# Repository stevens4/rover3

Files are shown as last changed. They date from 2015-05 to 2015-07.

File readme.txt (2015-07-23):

see documentation/Rover_3_Documentation.pdf

rover 3 functionality

need 6 AI and 12 DO, at least

hardware:
    1x raspberry pi 2 B (27 GPIO pins built in)
    2x thermocouple k-type amplifier
    1x pi breakout ribbon cable
    3x ADS1115 4chan 16b ADC  (interfaces via I2C, are stackable)
    1x power supply
    1x usb cable
    1x SD card, preloaded rasbian

analog inputs (sense):
    water thermocouple
    pooh main foreline pressure
    pooh source foreline pressure
    tigger source foreline pressure
    tigger buffer foreline pressure
    tigger main foreline pressure

digital output (relays):
    pooh water valve
    pooh source roughing
    pooh main roughing
    pooh source diffusion
    pooh main gate valve
    pooh source foreline valve
    tigger source foreline valve
    tigger main gate valve
    tigger diffusion pumps
    tigger main foreline valve
    tigger detector gauge
    tigger water valve

main features that we want:
	- real time logging of all AI & DO channels' values
		+ ability to plot history of values
		+ auto clean-up: compactify log based on age of entry
	- persist state of DIO in absence of pi power
	- automated interlocks 
		+ toggle a relay based on an AI value
		+ dispatch a message (clients, SMS) in this event
		+ add entry to status log
		+ configurable, configuration persists in absence of pi power
	- real time updating of a transcript of actions taken
	- rover client:
		+ subscribed to interlock events and DO toggle events
		+ can request current state of AI & DO

statusFile:
	timestamp:    [states of each DO + values of each AI]
	
transcript:
	timestamp:    [action that occurred in plain text. a capture of stdout]

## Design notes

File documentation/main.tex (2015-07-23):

\documentclass{article}
\usepackage[utf8]{inputenc}

\title{Rover 3 Documentation}
\author{Bobby Stevens}
\date{July 2015}

\usepackage{natbib}
\usepackage{graphicx}
\usepackage{url}
\usepackage{rotating}
\usepackage{multirow}

\begin{document}

\maketitle

\section{Introduction}
Rover is the name designated to the computer in the lab which controls the vacuum pumps and valves for both the Pooh and Tigger chambers. These things are not typically power cycled on a daily basis so their functionality is best contained in an infrequently used computer. Futhermore, these devices need to have interlocks (i.e. automatically be turned off based on some input sensor exceeding a set point) to ensure safe operation.

\subsection{Brief History of Rover}
This is the third incarnation of the Rover machine. The first, and longest running, was built on an Intel 386 based machine and was retired in 2011 after its graphics card failed. Thus ended the ``Good Dog'' era. It was replaced with a Windows XP machine running a LabView program attached to an NI-USB DAQ. This got the job done but had flaws such as requiring a sustained internet connection in order to authenticate LabView. This was the ``Bad Dog'' era. Rover 2 was replaced in 2015 by Rover 3. This marks the beginning of the ``Good Kitty'' era.

\section{Hardware Description}
We have a Raspberry Pi 2 (RP2) computer connected to a custom backplane board that buffers the DIO and provides the A2D chips for measurement by the Pi. The signals for the equipment toggle relays and instrumentation are then sent out to the individual racks for Pooh and Tigger. We will address each of these steps in their own subsection.

\subsection{The Raspberry Pi 2}
Rover 3 is built on a Raspberry Pi 2 model B (RP2). It is running Raspbian (raspberry optimized debian unix) with Gnome 2 installed on top. The RP2 was chosen for its low power consumption (5V @ 1A, max), built in DIO and I2C pins, and more than ample RAM.

Rover 3 interacts with the laboratory equipment through a custom backplane board, see section \ref{sect:backplane}, via its GPIO pins. The pin mapping is shown in figure \ref{fig:gpioPinMapping}. We have purchased a so-called ``cobbler'' board that has a ribbon cable plugged into the GPIO bank and connects to a labeled PCB.

\begin{figure}
\centering
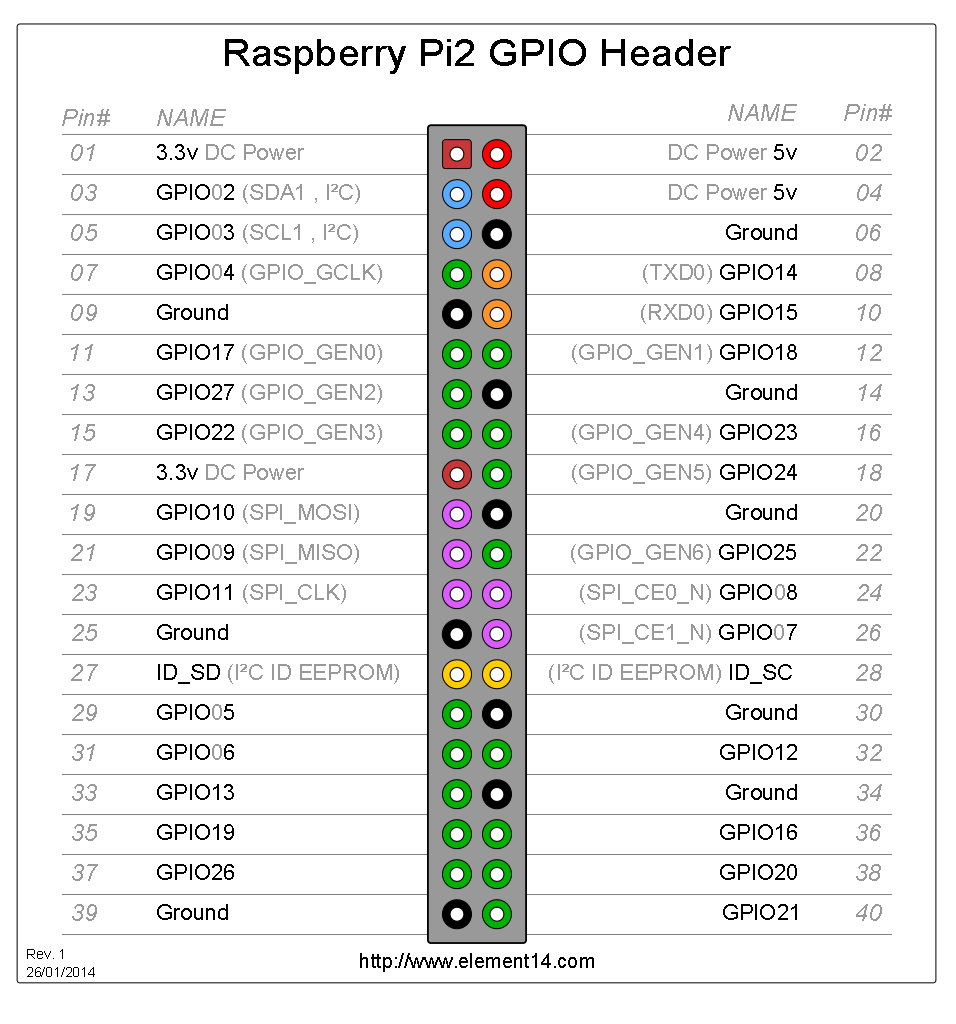
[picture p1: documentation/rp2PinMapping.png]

\caption{A mapping of the GPIO pins on the RP2 board. Interfacing at this level should not be necessary and the same information is printed on the ``cobbler'' board that is mounted to the backplane board. Source: element14.com}
\label{fig:gpioPinMapping}
\end{figure}

The monitor is attached by HDMI. The keyboard and mouse are both USB. Power is provided to the RP2 by a Motorola wall-to-USB transformer (better recognized as a cellphone charger) and plugged into the uninterurptable power supply.

\subsection{The Backplane Board}
\label{sect:backplane}
The RP2 cannot provide enough current on its DIO pins to toggle the relays (16mA max of RP2 compared to .02mA (steady state) and 6mA (switching) for relays). Thus we must buffer these DIO pins if we wish to control multiple relays at once. It also does not have any built-in analog-to-digital converter (ADC) so we will have to provide that functionality and serialize that data in some way. 

The backplane functional diagram is shown in figure \ref{fig:roverBreakout}. An attempt was made to keep the functional diagram and board layout as similar as possible to aid in troubleshooting when the need arises.

\begin{figure}
\centering
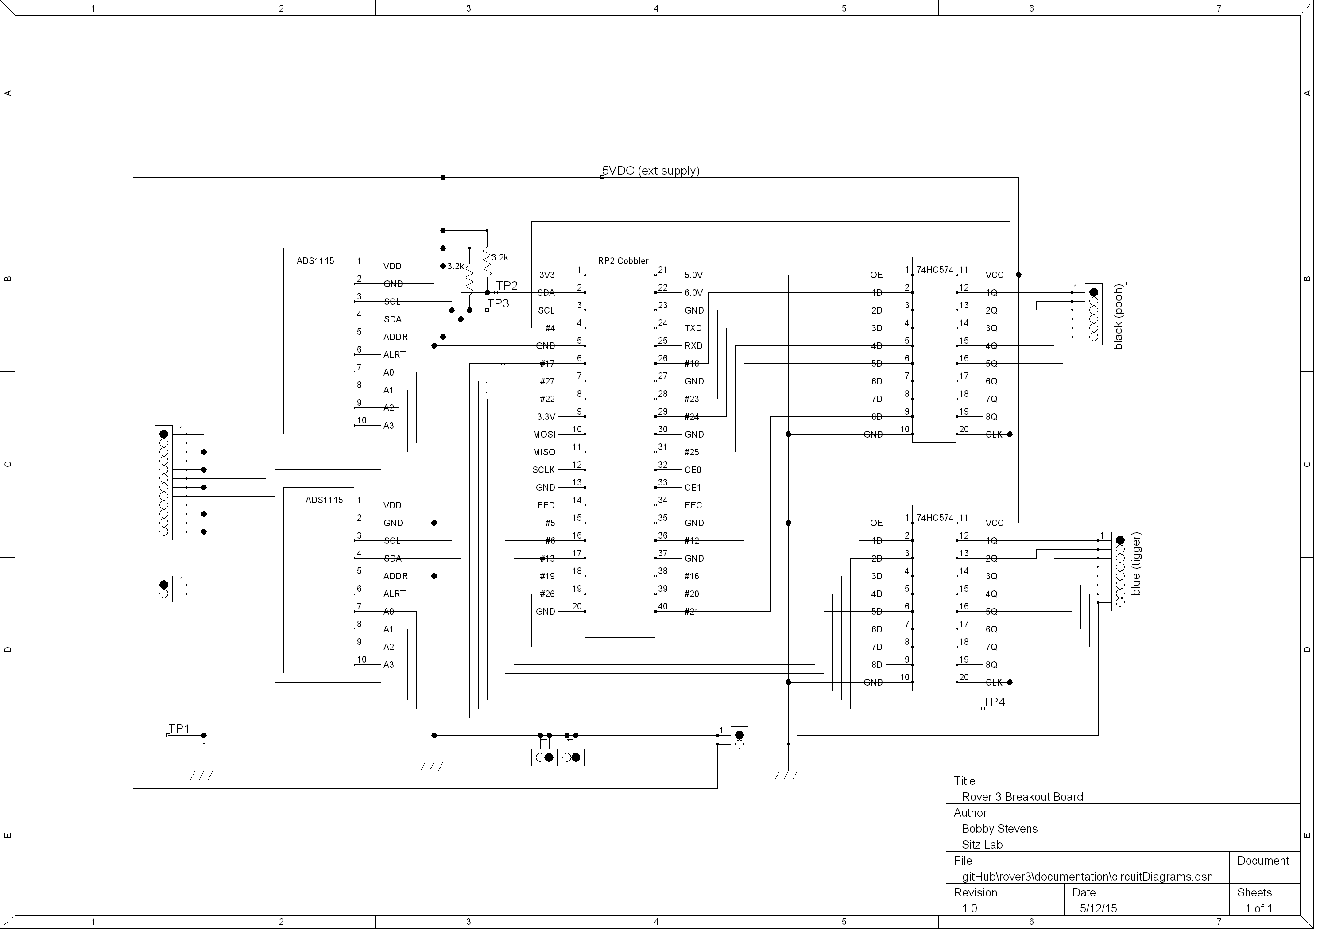
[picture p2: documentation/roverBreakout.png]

\caption{The functional diagram for the RP2 backplane board.}
\label{fig:roverBreakout}
\end{figure}

\subsubsection{DIO Buffering \& Relay Control}
The DIO control is handled on the right side of the backplane board.

A further need for buffering comes from the RP2's DIO reset state on power cycle. When the RP2 is rebooted, its DIO pins get written with an intermediate (TTL) level of 1.5V which is too high to read low and but will be read high by some buffer chips (e.g. 74LS241). This is undesirable because when the RP2 is booting we do not want every piece of equipment to turn on. Thus we use a clockable buffer. The 74HC574 chip has 8 inputs and 8 outputs with a clock pin that will ``write'' the input to the output only on a positive going transition. Thus we design our software (section \ref{sect:software}) to update the proper RP2 DIO pin then use a second DIO pin to clock the buffer thereby pushing that state to the relay or equipment.

The output pins of the 574 are then directly wired to the Pooh (black) and Tigger (blue) screw terminal blocks. The output pin numbers map 1-to-1 with the 574. See figure \ref{fig:roverBreakout}.

\subsubsection{ADC Implementation}
Analog input and digitization is handled on the left side of the backplane board, see figures \ref{fig:roverBreakout} and \ref{fig:roverBreakoutPicTop}.

As previously mentioned, the RP2 does not have any built-in ADC. We have 7 analog inputs that we need to interlock based upon their values. All but one of these needs to be a referenced single-ended (RSE) termination style which will require 6 ADCs. The remaining analog input needs to be measured in differential mode thus requiring 2 ADCs of its own. Thus we need 8 ADCs.

We will never need to respond very quickly to changes on any of these inputs. A response time of a few seconds is more than enough to establish safety with the diffusion pumps which take approximately 45 minutes to cool down anyways. Thus we do not need particularly fast ADCs.

Based on these requirements we can easily get by with a multiplexed ADC (multiple inputs are measured by 1 ADC in serial). TI's ADS1115 is precisely what we need. It has 4 inputs that will be multiplexed to a 16-bit 860SPS ADC. This information will be communicated by the I2C (or $I^2C$) interface. 

I2C is a serialized data communication protocol. This is done over two wires: a data wire (SDA) and a clock wire (SCL). Devices can only pull these wires low so a pull-up resistor is required to improve the time response (resistors R1 and R2 in figure \ref{fig:roverBreakout}). As in other protocols, there is a master and multiple slaves. For I2C each slave has a programmable 7-bit address. In the case of the ADS1115 the address pin will be tied low to make the address be 0x63 or tied high to make the address be 0x64. A key distinction for I2C is that any device can assert the clock pin low. This is important if you wish to truly understand how the communication works.

A timeline of how I2C works follows, refer to figure \ref{fig:i2cTiming} while reading. The master will send on SDA an address that it wants to either read or write from followed by a read/write bit. If that device is powered and on the lines it will respond the next clock cycle with the acknowledge or ``ack'' bit. Messages are limited to 8bits. If a read is specified the slave will load its data onto the SDA and clock SCL. If a write is specified the master will load data onto SDA and clock SCL. For more information on I2C see Horowitz and Hill.

\begin{figure}
\centering
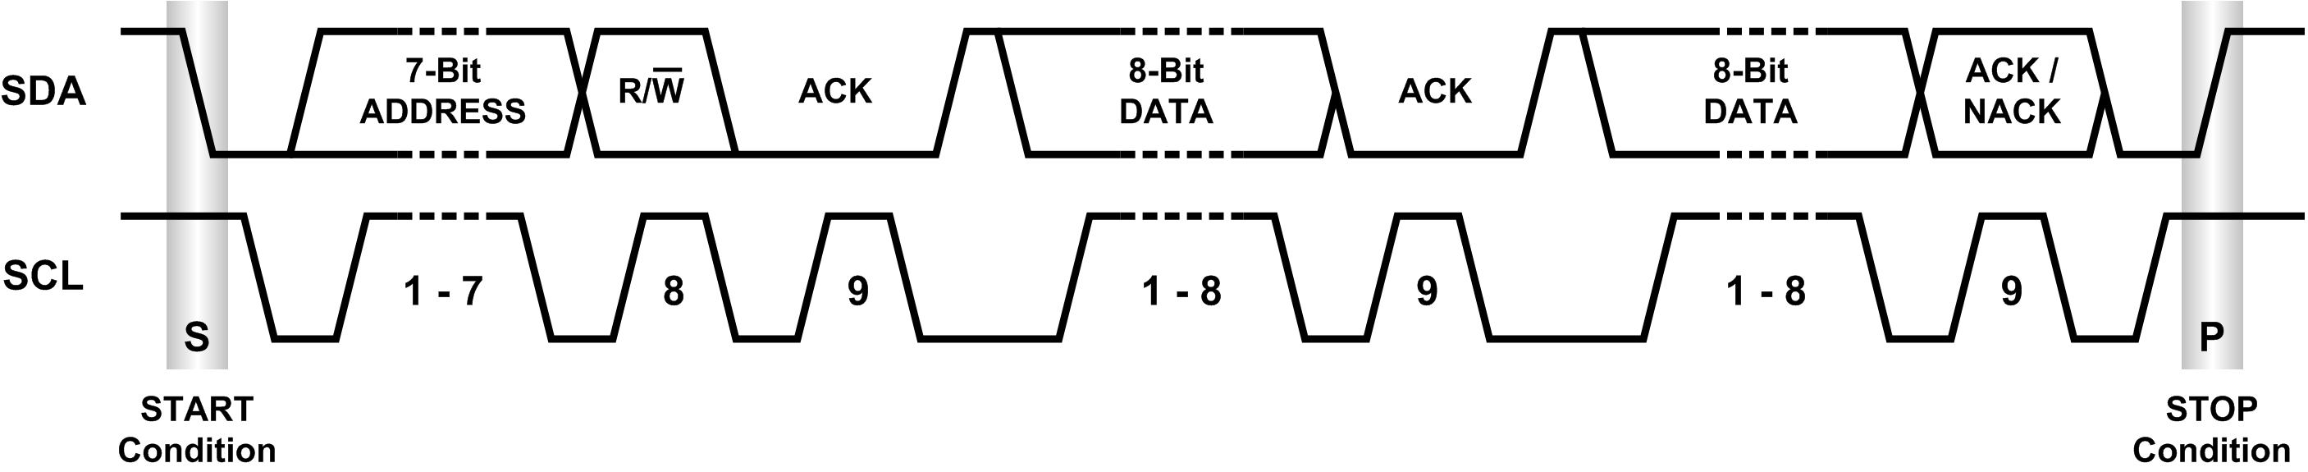
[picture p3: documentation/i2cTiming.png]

\caption{A timing diagram showing how I2C communication works. Source: cmpnet.com}
\label{fig:i2cTiming}
\end{figure}

To present the 4 inputs of the ADS1115 to the user each input is wired into a screw terminal and the adjacent terminal is connected to ground. This will allow you to connect RSE inputs by wiring into two adjacent terminals or differential by wiring into one terminal, skipping a terminal (ground), and wiring into the next. Be aware that if you need to measure differential you will have to reconfigure the input in software (see section \ref{sect:software}). There are two screw terminals on the AI side that are separated from the rest. These are the differential inputs that are wired into A2 and A3 on ADS1115-B.

\subsubsection{Wiring \& Test Points}
There was significant effort in making the wires color coded. The meanings for each color are listed in this table.

\begin{table}[h]
\begin{tabular}{r|l}
Wire Color & Function \\ \hline
Red & +5VDC \\ \hline
Black & Ground \\ \hline
Purple & clocking pin for 574 chips \\ \hline
Orange & I2C clock \\ \hline
Green & I2C data \\ \hline
Yellow, White, Lime Green, Blue & data lines, patterned in that order. \\
\end{tabular}
\end{table}

The test points are listed here:

\begin{table}[h]
\begin{tabular}{r|l}
Test Point (Color) & Function \\ \hline
TP0 (Black) & Ground  \\ \hline
TP1 (Purple) & DO clock \\ \hline
TP2 (Lime Green) & I2C clock \\ \hline
TP3 (Blue) & I2C data \\ 
\end{tabular}
\end{table}

\subsection{24VDC Relays Board}
This ancillary board should be viewed as a 24VDC ``booster'' to the 5VDC DIO lines from the 574. 4 pieces of equipment (Pooh gate valve, Pooh foreline valve, Tigger source foreline valve, and Tigger main foreline valve) need 24VDC to switch. It also contains a voltage divider on the 24V supply for a power sense line so that Rover can execute a power failure routine. The boosting is done with 4 Gordos 831A relays (datasheet included). 

\begin{figure}
\centering
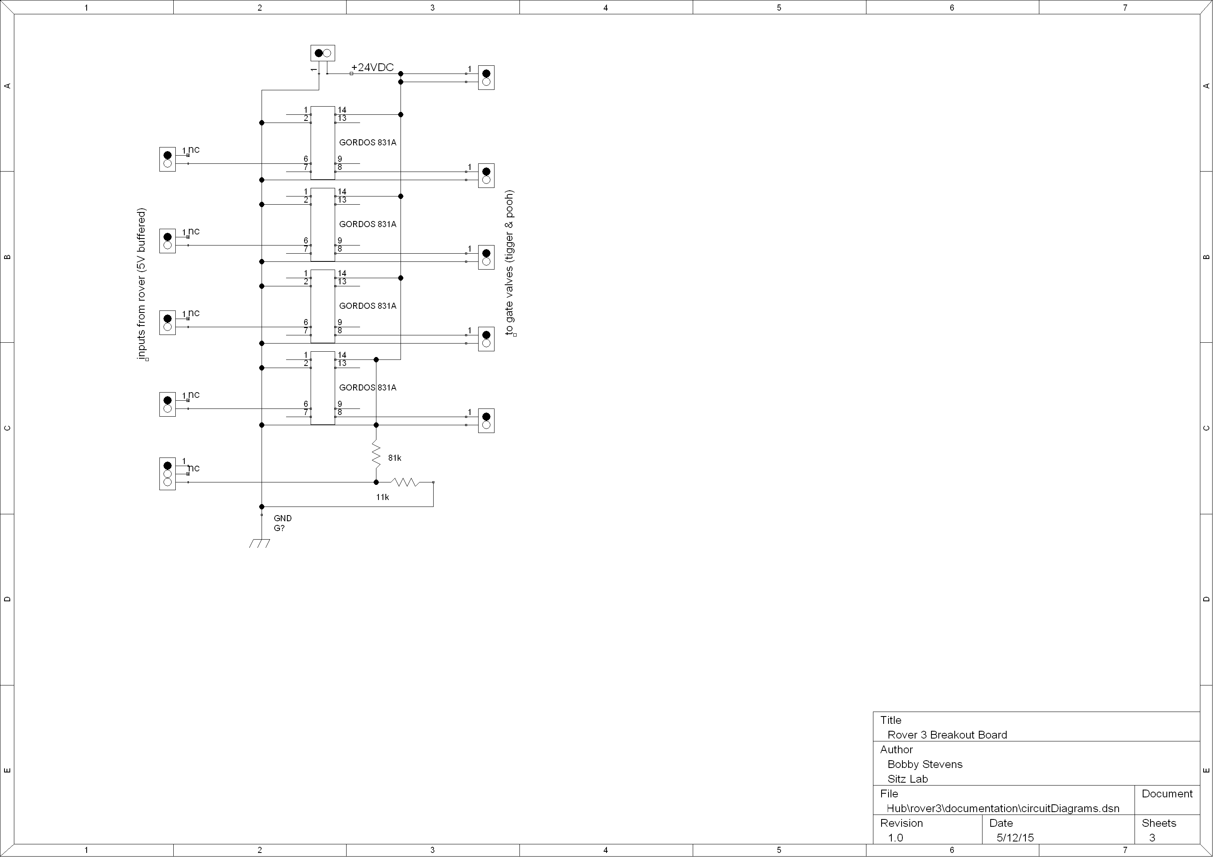
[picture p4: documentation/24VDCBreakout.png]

\caption{The functional diagram for the 24VDC relays board.}
\label{fig:24VDCBreakout}
\end{figure}

\subsection{120VAC Relays Board}
This is another ancillary board to switch 120VAC for 2 pieces of equipment on Tigger: the buffer and main gate valves. These are Crydom D2W solid state relays which take wall voltage input and connect the hot line to common through the equipment. The datasheet for these is included.

\begin{figure}
\centering
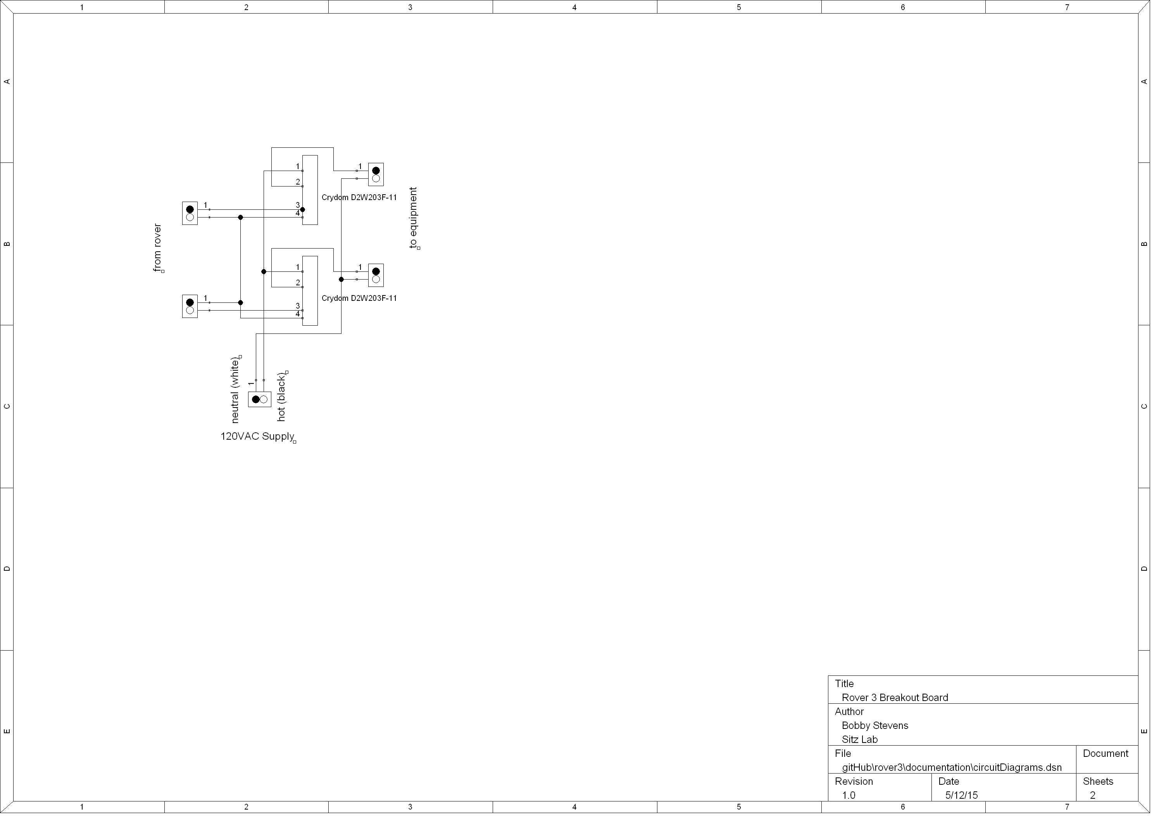
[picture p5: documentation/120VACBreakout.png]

\caption{The functional diagram for the 120VAC relays board.}
\label{fig:120VACBreakout}
\end{figure}

\section{Software Description}
\label{sect:software}
The software package for Rover 3 is available at \texttt{https://github.com/stevens4} \texttt{/rover3.git}. It is written in Python. The main program, \texttt{roverServer.py}, needs superuser permissions to access the DIO pins so it needs to be run as such, i.e. \texttt{sudo  python  roverServer.py}. An attempt was made to write the code in as modular a style as possible. From here we will discuss each module in turn.

\subsection{Standard Libraries}
The Rover 3 software requires 4 free-to-use libraries in order to run. Some of these libraries will need to be installed separately while others exist within the Github project. Here we will briefly state the function of each library within the project.

\noindent
\textbf{\emph{PySide:}} this is the GUI library used. It is a large project that maps the C++ QT framework to a python version. \textbf{Must be installed separately.}

\noindent
\textbf{\emph{RPi GPIO:}} allows control of the DIO pins from within python. \textbf{Must be installed separately.}

\noindent
\textbf{\emph{Adafruit ADS1x15:}} allows for interfacing with the ADS1115 chips within I2C protocol. \textbf{Bundled into project.}

\noindent
\textbf{\emph{Adafruit I2C:}} required for the Adafruit ADS1x15 library. \textbf{Bundled into project.}

\subsection{Custom Libraries}
The following libraries are files that were written by the author and are considered part of this project. They are libraries only in the sense that they are not executable on their own. We will spend a bit more time explaining these two libraries since customization will most likely take place at this level.

\subsubsection{\texttt{lowLevelLibrary.py}}
This library defines the hardware chips as software objects. It defines the \texttt{aiChannel}, \texttt{doChannel}, and \texttt{interlock} objects. The methods provided in each object should allow for any operations or configurations that are needed.

AIChannel objects can be configured only on initialization and will provide a mapped value based on the voltage that was previously measured. This mapping function is defined in the config, see section \ref{sect:config}, for each channel.

DOChannel objects have a specified RP2 pin they can toggle and a ``clock function'' they execute when a toggle is executed. The clock function is normally used to cycle the clock pin of the 574 chips. DOChannels can be toggled or polled for their current state and have a list of interlocks that can be reconfigured, added to, or removed from.

Interlock objects are owned by a DOChannel. An interlock is simply a logical statement concerning an AIChannel and a set point. \textbf{When this logical statement is \emph{true} the interlock will trip and turn the DOObject off.} Interlocks can be set from within the roverServer interface and are saved to a config directory to persist after the GUI is closed. 

\subsubsection{\texttt{customWidgets.py}}
This is the higher level library that defines customized PySide objects for the roverServer GUI with extended functionality to interface with hardware. It defines the \texttt{doControlRow} and \texttt{interlockConfig} objects.

\texttt{doControlRow} is a widget (see PySide documentation for terminology) that has the LED indicator, power toggle button, device label, interlock config button, and interlock override button. Each doObject has an associated doControlRow. The LED indicator comes from the SitzLabExpControl project but a copy is bundled into this package. 

\texttt{interlockConfig} is a dialog summoned from the doControlRow's interlock config button. This dialog allows the user to view and modify existing interlocks, remove interlocks, and add new interlocks. When the dialog is confirmed the interlocks are written to a config file and immediately take effect for this doControl object.

\subsubsection{\texttt{config.py}}
\label{sect:config}
The config file contains a dictionary of dictionaries for the analog inputs and digital outputs. This is where you can edit the GUI location and label text for both AIObjects and DOObjects and change which physical channels each are associated with. The AIChannels also have amplification factors for the ADC chip, the read rate, and the mapping function. The mapping function can either be ``poly'' (polynomial up to order 4) or ``exp'' (exponential). These functions will be applied to new measured voltages before they are sent to the GUI to be displayed as a value with units (e.g. pressure in milliTorr).

\subsection{Rover Server}
Rover server is mostly the GUI commands to initialize the environment. Most of this code will not need to be changed unless aesthetics are of concern. Key parts of the code that are not for GUI creation include the digital output clocking function \texttt{cycleDOClock()} and the A2D polling thread object \texttt{A2DThread()}. These are higher level functions that interface with the low level hardware and must be at the top level of code to ensure either (a) each DO toggle clocks the write pin or (b) each analog input is read in serial and conflicting calls are not made concurrently.

\section{Physical Connections}
Here we provide two tables for the controls (outputs of Rover) table \ref{tab:controls} and sensors (inputs to Rover) table \ref{tab:sense}. This information is also presented in figure \ref{fig:wiringDiagram}. Figure \ref{fig:roverOverhead} is a picture of the Rover system with helpful definitions of screw terminal labels.

\begin{figure}
\centering
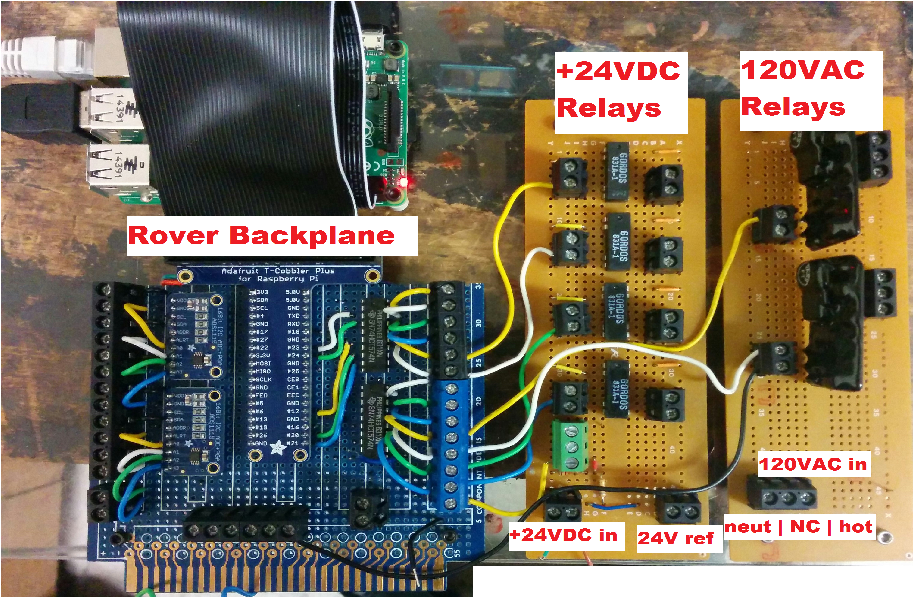
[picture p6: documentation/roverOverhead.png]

\caption{Labeled components of the hardware interface. The backplane board is more detailed in figure \ref{fig:roverOverhead2}. The ancillary 24VDC and 120VAC boards are labeled and their supply terminals marked.}
\label{fig:roverOverhead}
\end{figure}

\begin{figure}
\centering
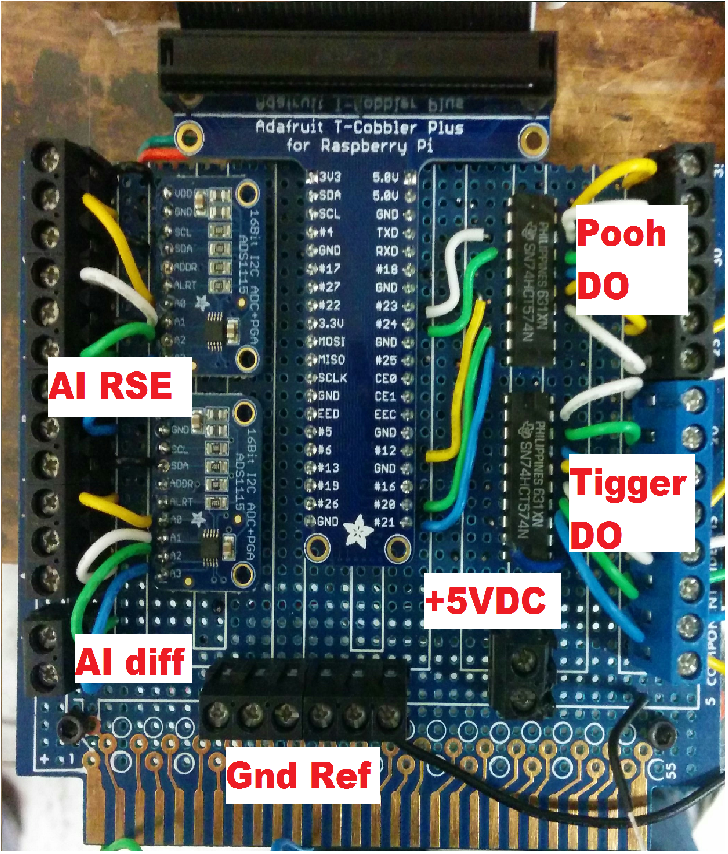
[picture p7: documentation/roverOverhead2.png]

\caption{Labeled components of the rover backplane board. On the left are the analog inputs and on the right are the digial outputs. The 12 unit long black screw terminal on the left are the AI RSE with every odd terminal connected to ground (note black wire indicating ground). The separate 2 unit terminal below is the AI differential input. The 6 unit black on the bottom are ground reference connections for the Pooh and Tigger devices, see table \ref{tab:controls}. The 2 unit black next to that is the +5VDC supply for the backplane components; both the ADS1115 and 574 chips are powered through this. The 6 unit black terminal on the right are the Pooh digital outputs. The 8 unit blue terminal is for Tigger with the exception being last position which is the lab power sense input that is connected to the green block on the +24VDC board.}
\label{fig:roverOverhead2}
\end{figure}

\begin{table}[]
\centering
\caption{the sensor connections for the Rover system}
\begin{tabular}{c|r|r|r|r}
& Label & ADS1115 pin & Screw Terminal & Wire ID \\ \hline
\multirow{2}{*}{pooh} & main foreline pressure & A0 & A1-2 & ?? \\ \cline{2-5}
& source foreline pressure & A1 & A3-4 & ?? \\ \hline \hline
\multirow{3}{*}{tigger} & main foreline pressure & A2 & A7-8 & ?? \\ \cline{2-5}
& source foreline pressure & B0 & A9-10 &  ?? \\ \cline{2-5}
& buffer foreline pressure & B1 & A11-12 & ?? \\ \hline \hline
both & water temp & B2-3 & B1-2 & \\ \cline{2-5}
& spare RSE & A3 & A5-6 & N/A
\end{tabular}
\label{tab:sense}
\end{table}

\begin{sidewaystable}[]
\centering
\caption{the control connections for the Rover system}
\begin{tabular}{c|r|r|r|r|r|r}
\parbox[t]{2mm}{\multirow{8}{*}{\rotatebox[origin=c]{90}{pooh}}} & Label & RP2 Pin & 574 Pin & Screw Terminal & Buffer Chip & Wire Color \\ \cline{2-7}
 & +5VDC reference & N/A & N/A & ?? & N/A & orange \\ \cline{2-7}
 & +24VDC reference & N/A & N/A & ?? & N/A & white \\ \cline{2-7}
 & +24VDC reference & N/A & N/A & ?? & N/A & white-black \\ \cline{2-7}
 & water valve & 18 & A1 & Black 1 & N/A & yellow \\ \cline{2-7}
 & main roughing pumps & 23 & A2 & Black 2 & N/A & black \\ \cline{2-7}
 & source roughing pumps & 24 & A3 & Black 3 & N/A & blue \\ \cline{2-7}
 & source diffusion pumps & 25 & A4 & Black 4 & N/A & brown \\ \cline{2-7}
 & main gate valve & 12 & A5 & Black 5 & Gordos-1 & purple \\ \cline{2-7}
 & main foreline valve & 16 & A6 & Black 6 & Gordos-2 & grey \\ \hline \hline
 & gnd reference & N/A & N/A & ?? & N/A & red \\ \cline{2-7}
\parbox[t]{2mm}{\multirow{7}{*}{\rotatebox[origin=c]{90}{tigger}}} & spare & 17 & B1 & Blue 1 & N/A & N/A \\ \cline{2-7}
 & water valve & 27 & B2 & Blue 2 & N/A & green \\ \cline{2-7}
 & diffusion pumps & 22 & B3 & Blue 3 & N/A & brown, blue, yellow, orange \\ \cline{2-7}
 & buffer foreline valve & 5 & B4 & Blue 4 & Crydom-1 & dark grey \\ \cline{2-7}
 & main gate valve & 6 & B5 & Blue 5 & Crydom-2 & white \\ \cline{2-7}
 & source foreline valve & 13 & B6 & Blue 6 & Gordos-3 & white-red \\ \cline{2-7}
 & main foreline valve & 19 & B7 & Blue 7 & Gordos-4 & white-green \\ \cline{2-7}
 & gnd reference & N/A & N/A & ?? & N/A & white-black \\ \cline{2-7}
 & gnd reference & N/A & N/A & ?? & N/A & white-white \\ \cline{2-7}
 & gnd reference & N/A & N/A & ?? & N/A & green \\ \hline \hline
\parbox[t]{2mm}{\multirow{3}{*}{\rotatebox[origin=c]{90}{general}}} & power sense & 26 & N/A & Blue 8 & 24VDC divide & N/A  \\ \cline{2-7}
\end{tabular}
\label{tab:controls}
\end{sidewaystable}

\begin{figure}
\centering
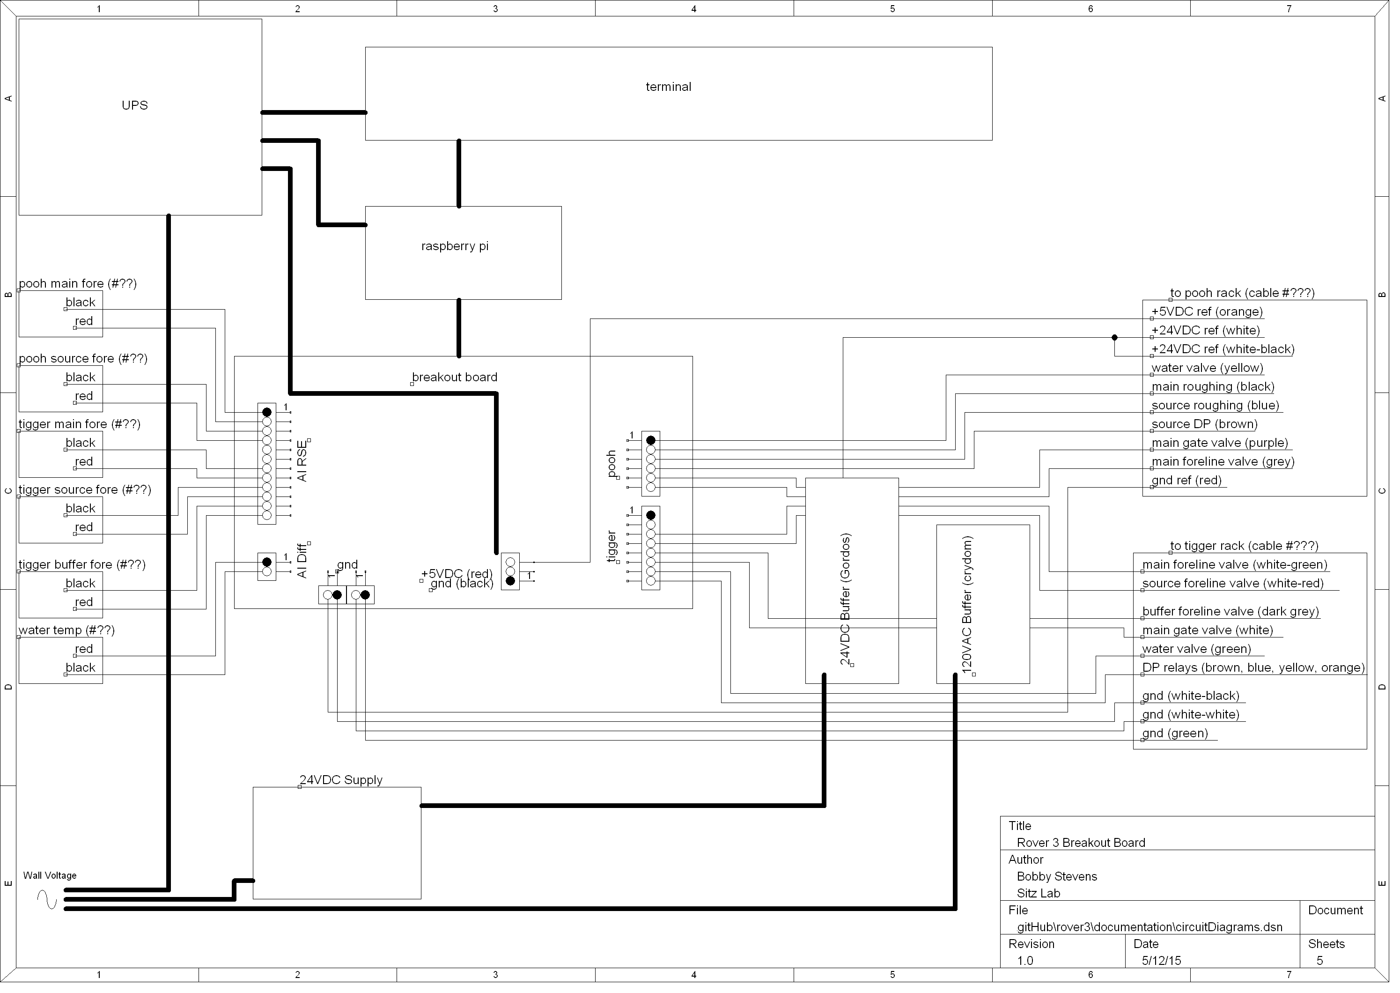
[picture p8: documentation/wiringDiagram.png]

\caption{}
\label{fig:wiringDiagram}
\end{figure}

\section{Start Up \& Common Usage}

\subsection{Rebooting Rover}
At startup the RP2 will not automatically log in. So you must first login as \textbf{\texttt{students}} with the password \textbf{\texttt{scatter12}}. Then you must manually start the graphical enviroment with \textbf{\texttt{startx}}. Once it has finished loading the desktop open a terminal window (icon on top bar on the left side) and navigate to \url{cd ~\Desktop\Rover3\}. Run the Rover Server with super user access: \texttt{sudo python roverServer.py}. It will resume its last current configuration. You will see a window like figure \ref{fig:ssMain}.

\begin{figure}
\centering
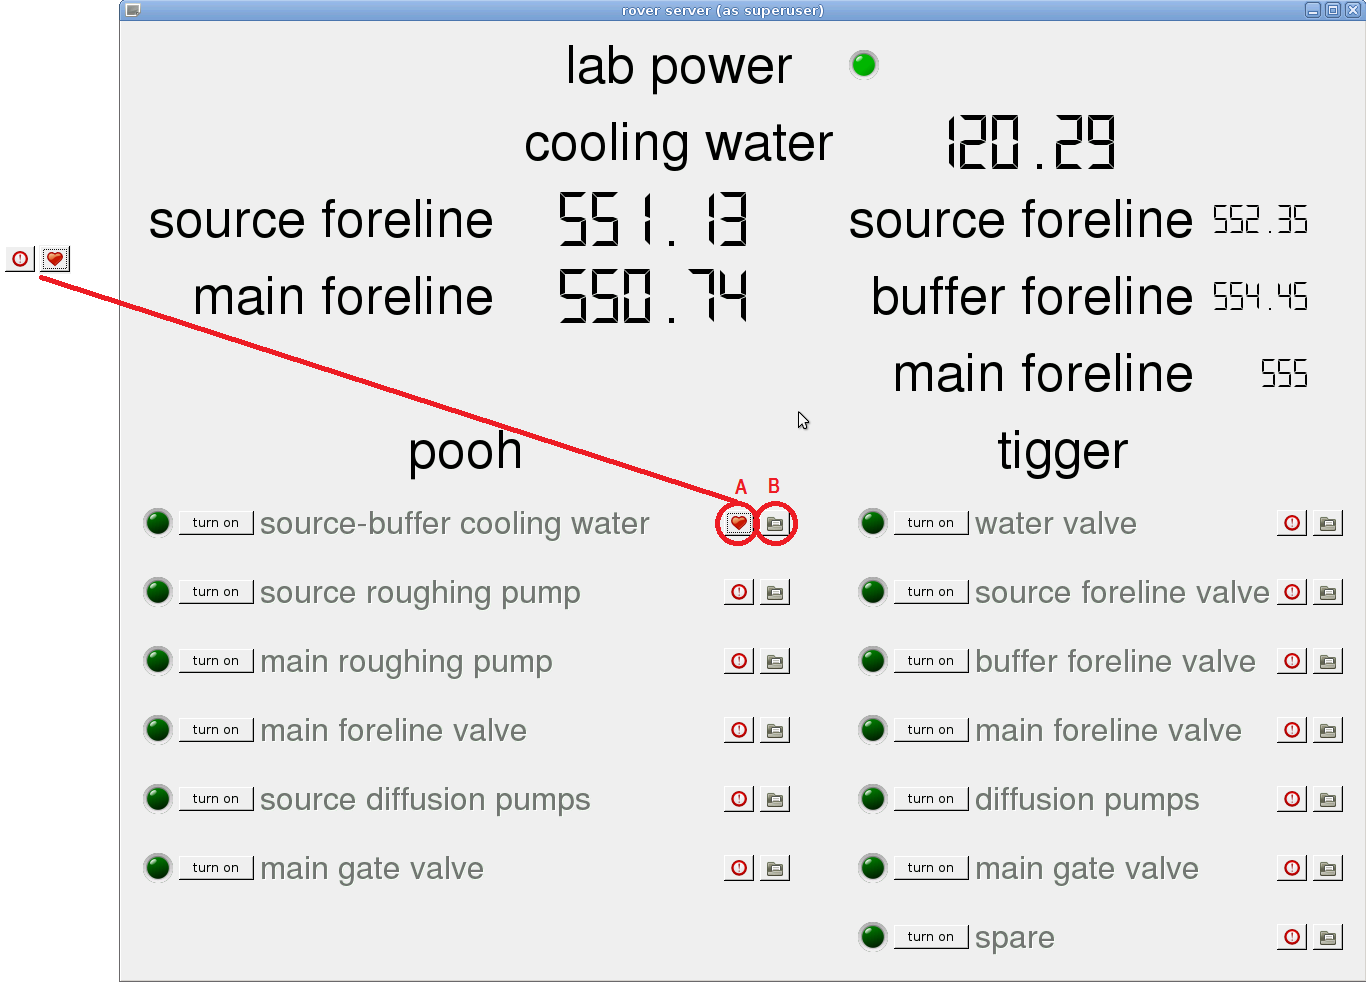
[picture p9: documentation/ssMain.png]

\caption{The main interface window for Rover 3. Sensor inputs along the top are displayed in millivolts when in debug mode or milliTorr/degrees celcius when not. Each relay control has its own row in the bottom half. Button A is the interlock override with the inset displaying the interlocks disabled icon (exclaimation point) and enabled icon (heart). Button B is the interlock configuration button which will spawn the window displayed in figure \ref{fig:ssInter} and is used to configure interlocks for that relay.}
\label{fig:ssMain}
\end{figure}

\subsection{Programming Interlocks}
To program interlocks first click the interlock config button for the device you wish to control (figure \ref{fig:ssMain}) which will spawn the interlock config window, figure \ref{fig:ssInter}. Set up a new interlock by picking which sensor you want to monitor followed by the logical level you want this sensor to remain relative to the set point. \textbf{When this logical statement is \emph{true} the interlock will trip and turn the DOObject off.} To create the interlock click the add button on the left. To commit the shown interlocks click the okay button. The interlocks are written to a config file for each control object and will persist after restarting Rover.

\begin{figure}
\centering
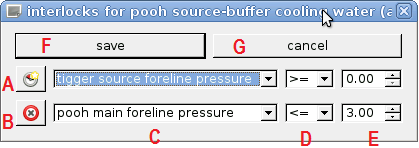
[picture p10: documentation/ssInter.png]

\caption{The interlock configuration window for Rover 3. Button A will create the interlock displayed in the top row. Button B will delete the interlock on that row. Combo boxes and spinbox C, D, and E are the input sensor, logical level on which to trip, and set point respectively. Remember that \textbf{true} statements cause the interlock to trip and shut the relay off. Button F will commit the current changes and button G will discard them.}
\label{fig:ssInter}
\end{figure}

If a device's interlocks are tripping and you wish to override you can disable the enforcement of interlocks with the interlock override button, see figure \ref{fig:ssMain}. A heart indicates that interlocks are being enforced while a exclaimation point indicates they are not. After an interlock trips and turns the device off the interlocks will be overriden for that device. This means that if an interlock trips you can simply force the device on by clicking `turn on' once more.

\subsection{Recovery from Power Loss}
Should the lab lose power unexpectedly Rover will be aware of it. Rover senses the lab power through a voltage divider on the +24VDC supply which is plugged direction into the wall (\textbf{NOT the uninterruptable power supply}). Rover has been programmed that in the event of power loss it should turn every device off and not turn devices back on once lab power is restored. Since both the 24VDC and 120VAC ancillary boards are powered directly from the wall those devices will shut off as soon as power is lost while the other devices will remain on for the approximate half second it takes Rover to respond. 

Rover is powered through the uninterruptable power supply so it should be able to remain on for roughly 6 hours without any lab power. If the UPS runs out Rover will lose power as well. If you anticipate power to be out for longer than 6 hours you should shut Rover down so that a corruption of the file system is not a possibility.

\section{Troubleshooting Guide}
Here we will outline the basic problems and solutions that have been observed during design and assembly. This is by no means a complete guide but will cover the most likely to occur problems.
\newline
\newline

If you are having problems with Rover your first step should be to rerun roverServer in debug mode: \texttt{sudo python roverServer.py debug}. This will write all the log status to the terminal window and not the log file as well as display all sensor readings in millivolts.
\newline
\newline

\noindent
\textbf{Symptom: the AI channels all read the same and it doesn't update (eg. 24). This should also be accompanied with an message in the transcript file 'lost connection to ADCs! Retrying in .5s...'.}

\noindent
\textbf{Cause: connection with the ADC units has been compromised.}

\noindent
\textbf{\emph{Solution 0:}} Check the physical connection between the sensors and the screw terminals.

\noindent
\textbf{\emph{Solution 1:}} First check the ribbon cable connection between the RP2 and backplane board.

\noindent
\textbf{\emph{Solution 2:}} the 5VDC supply for the backplane may not be working. Check its voltage at the black 2-screw terminal in the lower right quadrant.

\noindent
\textbf{\emph{Solution 3:}} Attach a oscilloscope between TP2 and TP0 and between TP3 and TP0. Close RoverServer.py. Execute \texttt{sudo i2cdetect -y 1}. The scope should display 16-bit bursts on both channels (see figure \ref{fig:i2cTiming}). If the logic levels are not sharp edges there is stray capacitance somewhere on either the clock or data lines. This causes the I2C bus to not register the addresses properly. This will be further confirmed by the i2cdetect program not showing an entry for 0x63 or 0x64 (the addresses of the ADCs). First check the connection on R1 and R2. These are pull-up resistors that should improve this voltage timing. Next check the connections on the I2C clock and data wires coming from the RP2 breakout to the ADCs (orange and green).
\newline
\newline

\noindent
\textbf{Symptom: python error - maximum recursion depth exceeded}

\noindent
\textbf{Cause: this is an antiquated version of \texttt{roverServer.py} which uses a recursive function to poll the ADCs in a thread.}

\noindent
\textbf{\emph{Solution 0:}} Make sure that someone didn't accidentally revert back to this recursive function. The class that does the ADC acquisition in \texttt{roverServer.py} should be a subclass of thread and should not end with a call to itself.
\newline
\newline

\noindent
\textbf{Symptom: turning a relay off is not actually toggling the device}

\noindent
\textbf{Cause: the relay control line is not working. A few malfunctioning devices could be causing this.}

\noindent
\textbf{\emph{Solution 0:}} Check your connections to devices at the screw terminals. See figure \ref{fig:wiringDiagram}. If they are all connected proceed.

\noindent
\textbf{\emph{Solution 1:}} First check the ribbon cable connection between the RP2 and backplane board.

\noindent
\textbf{\emph{Solution 2:}} the 5VDC supply for the backplane may not be working. Check its voltage at the black 2-screw terminal in the lower right quadrant.

\noindent
\textbf{\emph{Solution 3:}} Attach a oscilloscope between TP1 and TP0. This will be observing the clock pin sent to the 574 chips. The 574 will only update its output to match its input when this pin is clocked low to high. Toggle a device in \texttt{roverServer.py}. Does the scope show a clocking event? If no, check the connection between RP2 GPIO pin \#4 and pin \#11 on each of the 574s. If that is connected, check the source code for \texttt{roverServer.py} and make sure there is a method defined \texttt{clockPin} and it is being sent to each \texttt{digitalOutput} object upon initialization. If the 574s are both being clocked and their outputs are indeed not updating then the chip is faulty and needs to be replaced.

\noindent
\textbf{\emph{Solution 4:}} If the problem is localized to the Crydom 120VAC relays make sure that you are connecting a load across the relay's AC terminals. These relays won't actually power unless it sees a load and a DVM doesn't count!

\end{document}

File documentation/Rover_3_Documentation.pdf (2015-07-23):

# Rover 3 Documentation

Bobby Stevens

July 2015

## 1 Introduction

Rover is the name designated to the computer in the lab which controls the vacuum pumps and valves for both the Pooh and Tigger chambers. These things are not typically power cycled on a daily basis so their functionality is best contained in an infrequently used computer. Futhermore, these devices need to have interlocks (i.e. automatically be turned off based on some input sensor exceeding a set point) to ensure safe operation.

### 1.1 Brief History of Rover

This is the third incarnation of the Rover machine. The first, and longest running, was built on an Intel 386 based machine and was retired in 2011 after its graphics card failed. Thus ended the “Good Dog” era. It was replaced with a Windows XP machine running a LabView program attached to an NI-USB DAQ. This got the job done but had flaws such as requiring a sustained internet connection in order to authenticate LabView. This was the “Bad Dog” era. Rover 2 was replaced in 2015 by Rover 3. This marks the beginning of the “Good Kitty” era.

## 2 Hardware Description

We have a Raspberry Pi 2 (RP2) computer connected to a custom backplane board that buffers the DIO and provides the A2D chips for measurement by the Pi. The signals for the equipment toggle relays and instrumentation are then sent out to the individual racks for Pooh and Tigger. We will address each of these steps in their own subsection.

### 2.1 The Raspberry Pi 2

Rover 3 is built on a Raspberry Pi 2 model B (RP2). It is running Raspbian (raspberry optimized debian unix) with Gnome 2 installed on top. The RP2 was chosen for its low power consumption (5V @ 1A, max), built in DIO and I2C pins, and more than ample RAM.

1


Figure 1: A mapping of the GPIO pins on the RP2 board. Interfacing at this level should not be necessary and the same information is printed on the “cobbler” board that is mounted to the backplane board. Source: element14.com

Rover 3 interacts with the laboratory equipment through a custom backplane board, see section 2.2, via its GPIO pins. The pin mapping is shown in figure 1. We have purchased a so-called “cobbler” board that has a ribbon cable plugged into the GPIO bank and connects to a labeled PCB.
The monitor is attached by HDMI. The keyboard and mouse are both USB. Power is provided to the RP2 by a Motorola wall-to-USB transformer (better recognized as a cellphone charger) and plugged into the uninterurptable power supply.

2

### 2.2 The Backplane Board

The RP2 cannot provide enough current on its DIO pins to toggle the relays (16mA max of RP2 compared to .02mA (steady state) and 6mA (switching) for relays). Thus we must buffer these DIO pins if we wish to control multiple relays at once. It also does not have any built-in analog-to-digital converter (ADC) so we will have to provide that functionality and serialize that data in some way.
The backplane functional diagram is shown in figure 2. An attempt was made to keep the functional diagram and board layout as similar as possible to aid in troubleshooting when the need arises.

### 2.2.1 DIO Buffering & Relay Control

The DIO control is handled on the right side of the backplane board.
A further need for buffering comes from the RP2’s DIO reset state on power cycle. When the RP2 is rebooted, its DIO pins get written with an intermediate (TTL) level of 1.5V which is too high to read low and but will be read high by some buffer chips (e.g. 74LS241). This is undesirable because when the RP2 is booting we do not want every piece of equipment to turn on. Thus we use a clockable buffer. The 74HC574 chip has 8 inputs and 8 outputs with a clock pin that will “write” the input to the output only on a positive going transition. Thus we design our software (section 3) to update the proper RP2 DIO pin then use a second DIO pin to clock the buffer thereby pushing that state to the relay or equipment.
The output pins of the 574 are then directly wired to the Pooh (black) and Tigger (blue) screw terminal blocks. The output pin numbers map 1-to-1 with the 574. See figure 2.

### 2.2.2 ADC Implementation

Analog input and digitization is handled on the left side of the backplane board, see figures 2 and ??.
As previously mentioned, the RP2 does not have any built-in ADC. We have 7 analog inputs that we need to interlock based upon their values. All but one of these needs to be a referenced single-ended (RSE) termination style which will require 6 ADCs. The remaining analog input needs to be measured in differential mode thus requiring 2 ADCs of its own. Thus we need 8 ADCs. We will never need to respond very quickly to changes on any of these inputs. A response time of a few seconds is more than enough to establish safety with the diffusion pumps which take approximately 45 minutes to cool down anyways. Thus we do not need particularly fast ADCs.
Based on these requirements we can easily get by with a multiplexed ADC (multiple inputs are measured by 1 ADC in serial). TI’s ADS1115 is precisely what we need. It has 4 inputs that will be multiplexed to a 16-bit 860SPS ADC. This information will be communicated by the I2C (or I

2C) interface.

3

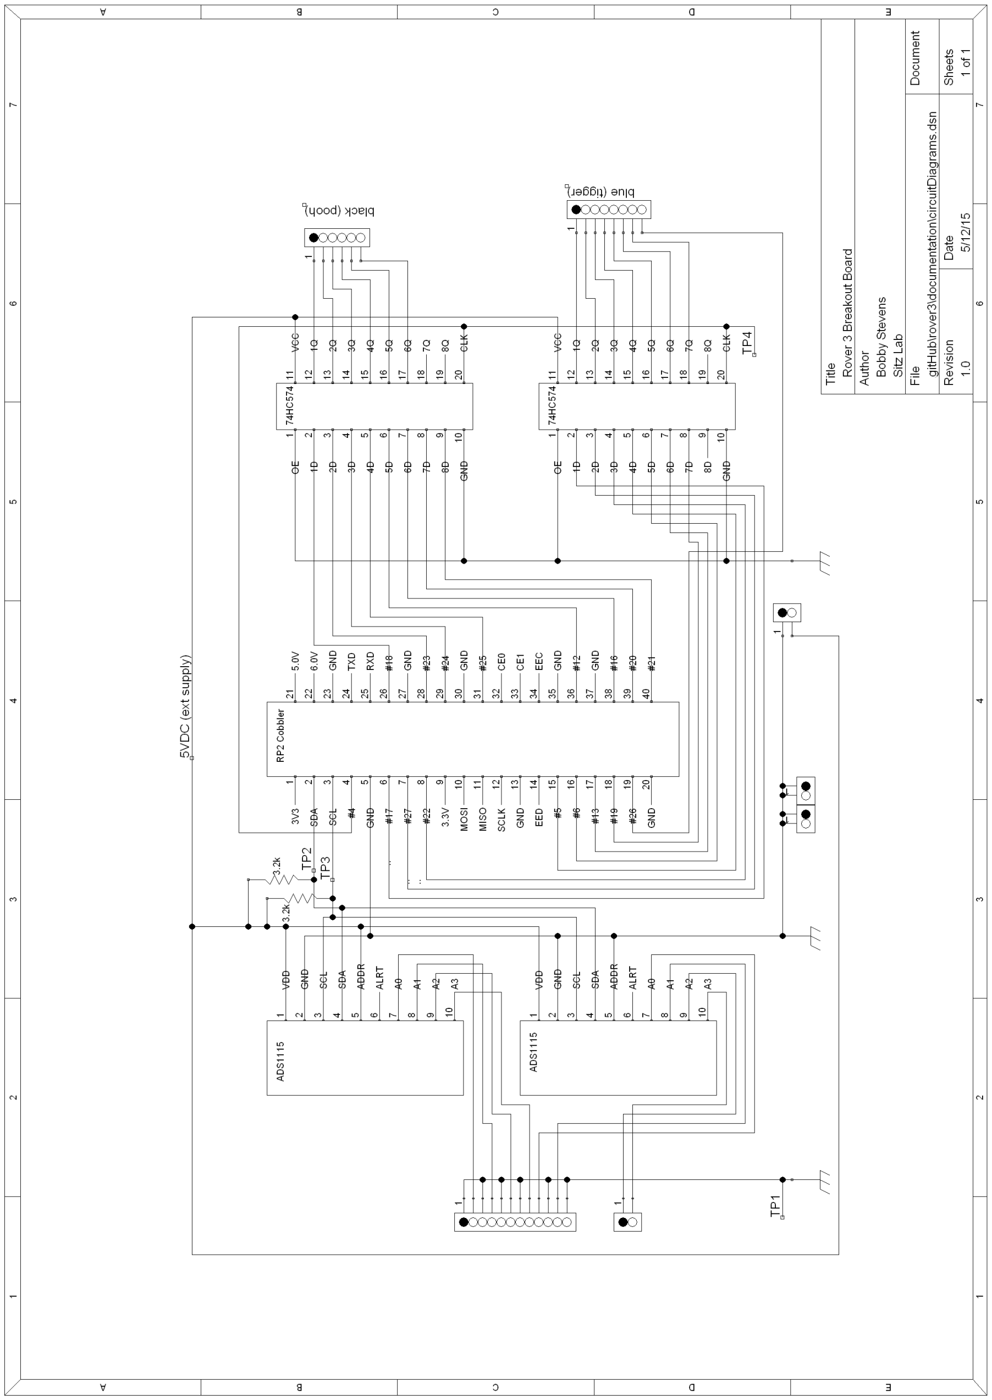
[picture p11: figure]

Figure 2: The functional diagram for the RP2 backplane board.

4

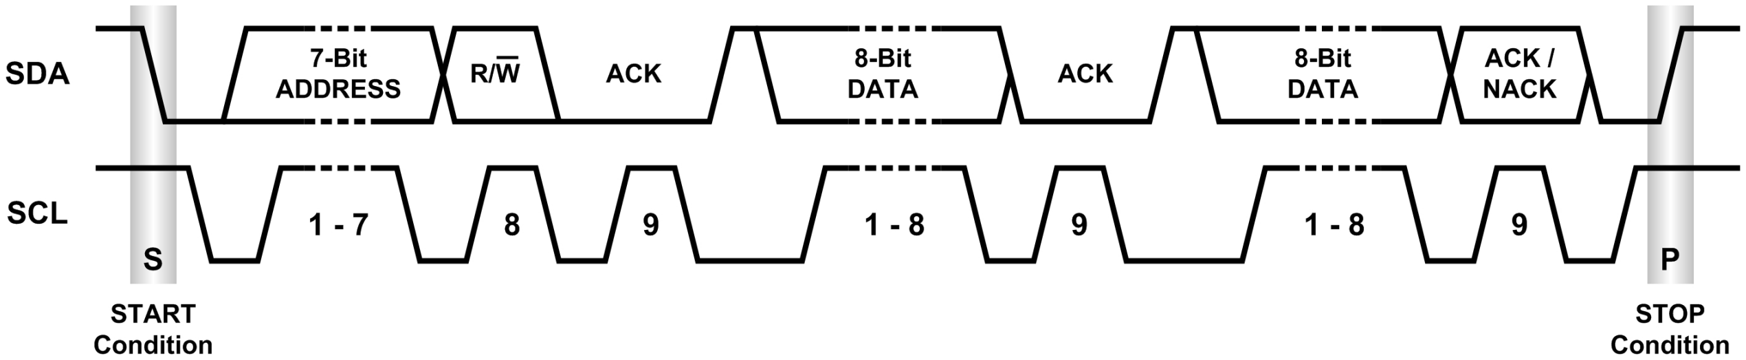
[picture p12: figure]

Figure 3: A timing diagram showing how I2C communication works. Source: cmpnet.com

I2C is a serialized data communication protocol. This is done over two wires: a data wire (SDA) and a clock wire (SCL). Devices can only pull these wires low so a pull-up resistor is required to improve the time response (resistors R1 and R2 in figure 2). As in other protocols, there is a master and multiple slaves. For I2C each slave has a programmable 7-bit address. In the case of the ADS1115 the address pin will be tied low to make the address be 0x63 or tied high to make the address be 0x64. A key distinction for I2C is that any device can assert the clock pin low. This is important if you wish to truly understand how the communication works.
A timeline of how I2C works follows, refer to figure 3 while reading. The master will send on SDA an address that it wants to either read or write from followed by a read/write bit. If that device is powered and on the lines it will respond the next clock cycle with the acknowledge or “ack” bit. Messages are limited to 8bits. If a read is specified the slave will load its data onto the SDA and clock SCL. If a write is specified the master will load data onto SDA and clock SCL. For more information on I2C see Horowitz and Hill.
To present the 4 inputs of the ADS1115 to the user each input is wired into a screw terminal and the adjacent terminal is connected to ground. This will allow you to connect RSE inputs by wiring into two adjacent terminals or differential by wiring into one terminal, skipping a terminal (ground), and wiring into the next. Be aware that if you need to measure differential you will have to reconfigure the input in software (see section 3). There are two screw terminals on the AI side that are separated from the rest. These are the differential inputs that are wired into A2 and A3 on ADS1115-B.

### 2.2.3 Wiring & Test Points

There was significant effort in making the wires color coded. The meanings for each color are listed in this table.
The test points are listed here:

2.3 24VDC Relays Board

This ancillary board should be viewed as a 24VDC “booster” to the 5VDC DIO lines from the 574. 4 pieces of equipment (Pooh gate valve, Pooh foreline valve, Tigger source foreline valve, and Tigger main foreline valve) need 24VDC to

5

Wire Color | Function
Red | +5VDC
Black | Ground
Purple | clocking pin for 574 chips
Orange | I2C clock
Green | I2C data
Yellow, White, Lime Green, Blue | data lines, patterned in that order.
Test Point (Color) | Function
TP0 (Black) | Ground
TP1 (Purple) | DO clock
TP2 (Lime Green) | I2C clock
TP3 (Blue) | I2C data

switch. It also contains a voltage divider on the 24V supply for a power sense line so that Rover can execute a power failure routine. The boosting is done with 4 Gordos 831A relays (datasheet included).

2.4 120VAC Relays Board

This is another ancillary board to switch 120VAC for 2 pieces of equipment on Tigger: the buffer and main gate valves. These are Crydom D2W solid state relays which take wall voltage input and connect the hot line to common through the equipment. The datasheet for these is included.

## 3 Software Description

The software package for Rover 3 is available at https://github.com/stevens4/rover3.git. It is written in Python. The main program, roverServer.py, needs superuser permissions to access the DIO pins so it needs to be run as such, i.e. sudo python roverServer.py. An attempt was made to write the code in as modular a style as possible. From here we will discuss each module in turn.

### 3.1 Standard Libraries

The Rover 3 software requires 4 free-to-use libraries in order to run. Some of these libraries will need to be installed separately while others exist within the Github project. Here we will briefly state the function of each library within the project.
PySide: this is the GUI library used. It is a large project that maps the C++ QT framework to a python version. Must be installed separately.
RPi GPIO: allows control of the DIO pins from within python. Must be installed separately.

6

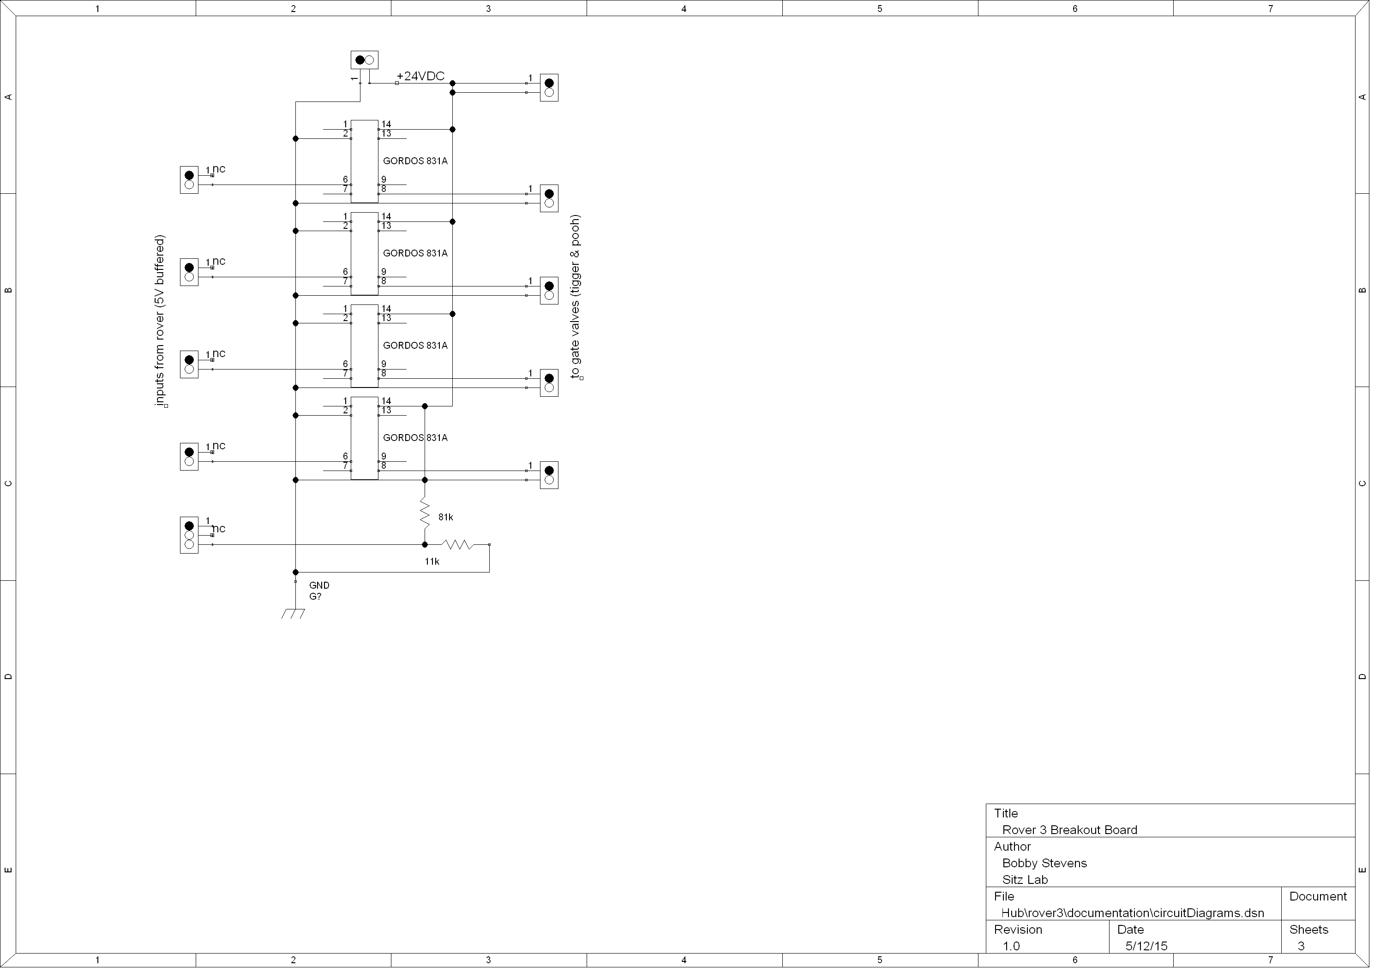
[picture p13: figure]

Figure 4: The functional diagram for the 24VDC relays board.

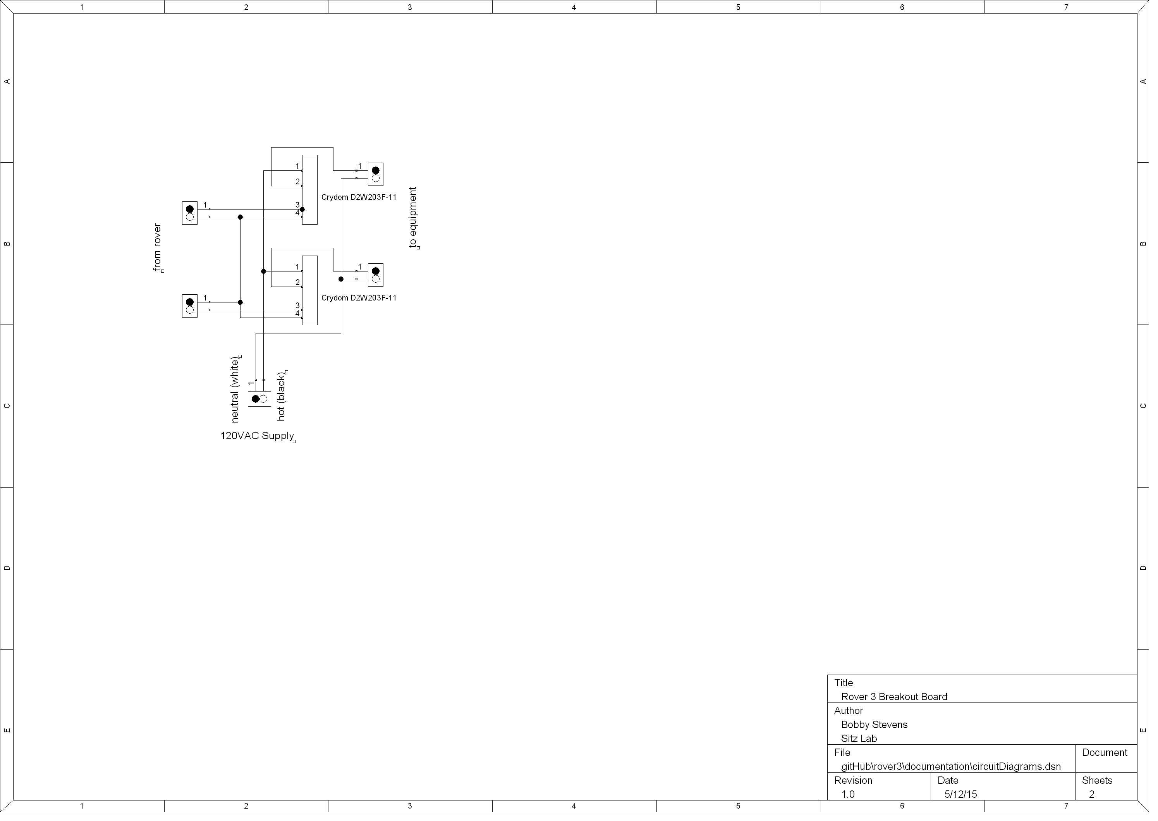
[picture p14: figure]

Figure 5: The functional diagram for the 120VAC relays board.

7

Adafruit ADS1x15: allows for interfacing with the ADS1115 chips within I2C protocol. Bundled into project.
Adafruit I2C: required for the Adafruit ADS1x15 library. Bundled into project.

### 3.2 Custom Libraries

The following libraries are files that were written by the author and are considered part of this project. They are libraries only in the sense that they are not executable on their own. We will spend a bit more time explaining these two libraries since customization will most likely take place at this level.

### 3.2.1 lowLevelLibrary.py

This library defines the hardware chips as software objects. It defines the aiChannel, doChannel, and interlock objects. The methods provided in each object should allow for any operations or configurations that are needed. AIChannel objects can be configured only on initialization and will provide a mapped value based on the voltage that was previously measured. This mapping function is defined in the config, see section 3.2.3, for each channel.
DOChannel objects have a specified RP2 pin they can toggle and a “clock function” they execute when a toggle is executed. The clock function is normally used to cycle the clock pin of the 574 chips. DOChannels can be toggled or polled for their current state and have a list of interlocks that can be reconfigured, added to, or removed from.
Interlock objects are owned by a DOChannel. An interlock is simply a logical statement concerning an AIChannel and a set point. When this logical statement is true the interlock will trip and turn the DOObject off. Interlocks can be set from within the roverServer interface and are saved to a config directory to persist after the GUI is closed.

### 3.2.2 customWidgets.py

This is the higher level library that defines customized PySide objects for the roverServer GUI with extended functionality to interface with hardware. It defines the doControlRow and interlockConfig objects.
doControlRow is a widget (see PySide documentation for terminology) that has the LED indicator, power toggle button, device label, interlock config button, and interlock override button. Each doObject has an associated doControlRow. The LED indicator comes from the SitzLabExpControl project but a copy is bundled into this package.
interlockConfig is a dialog summoned from the doControlRow’s interlock config button. This dialog allows the user to view and modify existing interlocks, remove interlocks, and add new interlocks. When the dialog is confirmed the interlocks are written to a config file and immediately take effect for this doControl object.

8

Table 1: the sensor connections for the Rover system
| Label | ADS1115 pin | Screw Terminal | Wire ID
pooh | main foreline pressure | A0 | A1-2 | ??
| source foreline pressure | A1 | A3-4 | ??
tigger | main foreline pressure | A2 | A7-8 | ??
| source foreline pressure | B0 | A9-10 | ??
| buffer foreline pressure | B1 | A11-12 | ??
both | water temp | B2-3 | B1-2
| spare RSE | A3 | A5-6 | N/A

### 3.2.3 config.py

The config file contains a dictionary of dictionaries for the analog inputs and digital outputs. This is where you can edit the GUI location and label text for both AIObjects and DOObjects and change which physical channels each are associated with. The AIChannels also have amplification factors for the ADC chip, the read rate, and the mapping function. The mapping function can either be “poly” (polynomial up to order 4) or “exp” (exponential). These functions will be applied to new measured voltages before they are sent to the GUI to be displayed as a value with units (e.g. pressure in milliTorr).

### 3.3 Rover Server

Rover server is mostly the GUI commands to initialize the environment. Most of this code will not need to be changed unless aesthetics are of concern. Key parts of the code that are not for GUI creation include the digital output clocking function cycleDOClock() and the A2D polling thread object A2DThread(). These are higher level functions that interface with the low level hardware and must be at the top level of code to ensure either (a) each DO toggle clocks the write pin or (b) each analog input is read in serial and conflicting calls are not made concurrently.

## 4 Physical Connections

Here we provide two tables for the controls (outputs of Rover) table 2 and sensors (inputs to Rover) table 1. This information is also presented in figure
8. Figure 6 is a picture of the Rover system with helpful definitions of screw terminal labels.

9

Table 2: the control connections for the Rover system

Label RP2 Pin 574 Pin Screw Terminal Buffer Chip Wire Color

+5VDC reference N/A N/A ?? N/A orange
+24VDC reference N/A N/A ?? N/A white
+24VDC reference N/A N/A ?? N/A white-black

water valve 18 A1 Black 1 N/A yellow

main roughing pumps 23 A2 Black 2 N/A black

source roughing pumps 24 A3 Black 3 N/A blue

source diffusion pumps 25 A4 Black 4 N/A brown
main gate valve 12 A5 Black 5 Gordos-1 purple

main foreline valve 16 A6 Black 6 Gordos-2 grey

gnd reference N/A N/A ?? N/A red

spare 17 B1 Blue 1 N/A N/A
water valve 27 B2 Blue 2 N/A green
diffusion pumps 22 B3 Blue 3 N/A brown, blue, yellow, orange

buffer foreline valve 5 B4 Blue 4 Crydom-1 dark grey

main gate valve 6 B5 Blue 5 Crydom-2 white
source foreline valve 13 B6 Blue 6 Gordos-3 white-red
main foreline valve 19 B7 Blue 7 Gordos-4 white-green
gnd reference N/A N/A ?? N/A white-black
gnd reference N/A N/A ?? N/A white-white

gnd reference N/A N/A ?? N/A green

10

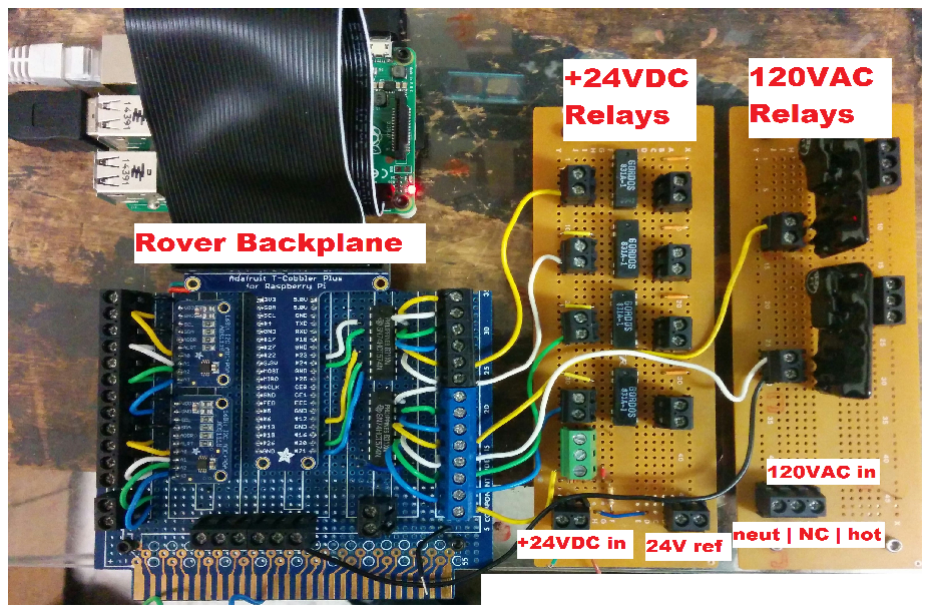
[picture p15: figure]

Figure 6: Labeled components of the hardware interface. The backplane board is more detailed in figure 7. The ancillary 24VDC and 120VAC boards are labeled and their supply terminals marked.

## 5 Start Up & Common Usage

### 5.1 Rebooting Rover

At startup the RP2 will not automatically log in. So you must first login as students with the password scatter12. Then you must manually start the graphical enviroment with startx. Once it has finished loading the desktop open a terminal window (icon on top bar on the left side) and navigate to cd~\Desktop\Rover3\. Run the Rover Server with super user access: sudo python roverServer.py. It will resume its last current configuration. You will see a window like figure 9.

### 5.2 Programming Interlocks

To program interlocks first click the interlock config button for the device you wish to control (figure 9) which will spawn the interlock config window, figure 10. Set up a new interlock by picking which sensor you want to monitor followed by the logical level you want this sensor to remain relative to the set point. When this logical statement is true the interlock will trip and turn the DOObject off. To create the interlock click the add button on the left. To commit the shown interlocks click the okay button. The interlocks are written to a config file for each control object and will persist after restarting Rover. If a device’s interlocks are tripping and you wish to override you can disable

11

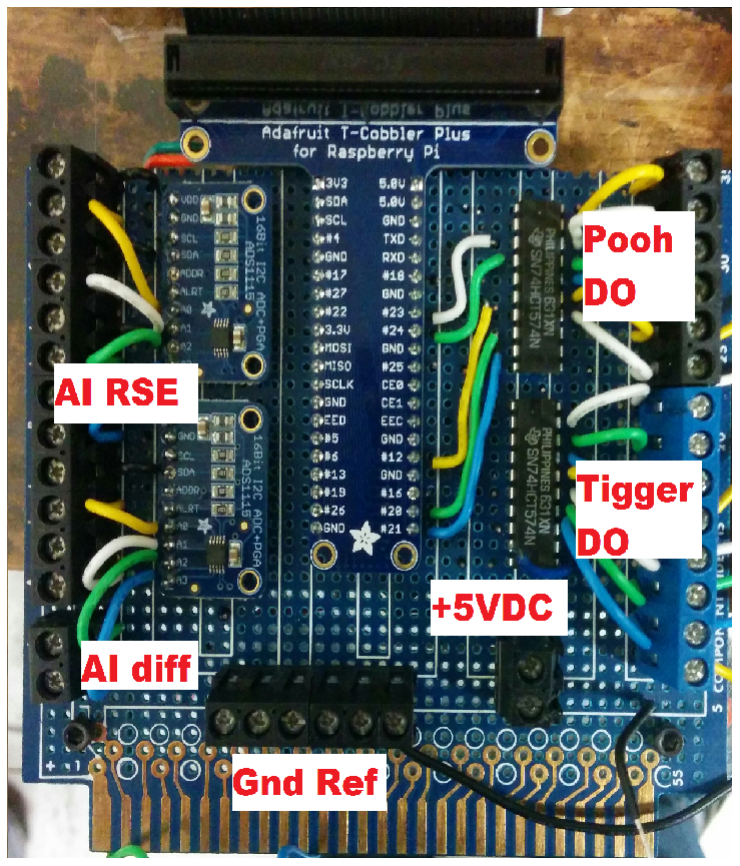
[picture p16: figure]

Figure 7: Labeled components of the rover backplane board. On the left are the analog inputs and on the right are the digial outputs. The 12 unit long black screw terminal on the left are the AI RSE with every odd terminal connected to ground (note black wire indicating ground). The separate 2 unit terminal below is the AI differential input. The 6 unit black on the bottom are ground reference connections for the Pooh and Tigger devices, see table 2. The 2 unit black next to that is the +5VDC supply for the backplane components; both the ADS1115 and 574 chips are powered through this. The 6 unit black terminal on the right are the Pooh digital outputs. The 8 unit blue terminal is for Tigger with the exception being last position which is the lab power sense input that is connected to the green block on the +24VDC board.

12


Figure 8:

the enforcement of interlocks with the interlock override button, see figure 9. A heart indicates that interlocks are being enforced while a exclaimation point indicates they are not. After an interlock trips and turns the device off the interlocks will be overriden for that device. This means that if an interlock trips you can simply force the device on by clicking ‘turn on’ once more.

### 5.3 Recovery from Power Loss

Should the lab lose power unexpectedly Rover will be aware of it. Rover senses the lab power through a voltage divider on the +24VDC supply which is plugged direction into the wall (NOT the uninterruptable power supply). Rover has been programmed that in the event of power loss it should turn every device off and not turn devices back on once lab power is restored. Since both the 24VDC and 120VAC ancillary boards are powered directly from the wall those devices will shut off as soon as power is lost while the other devices will remain on for the approximate half second it takes Rover to respond.
Rover is powered through the uninterruptable power supply so it should be able to remain on for roughly 6 hours without any lab power. If the UPS runs out Rover will lose power as well. If you anticipate power to be out for longer than 6 hours you should shut Rover down so that a corruption of the file system is not a possibility.

13

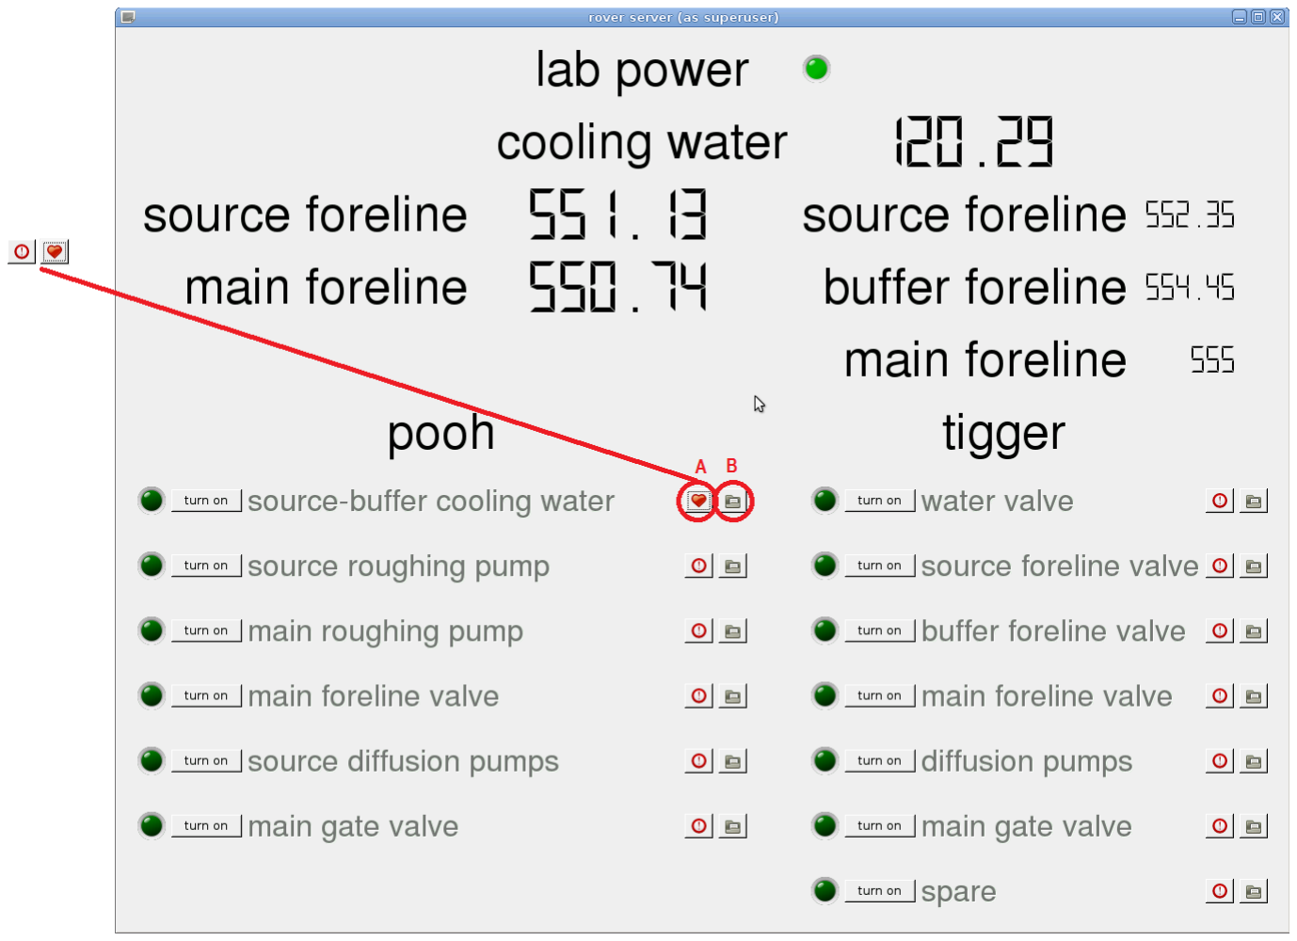
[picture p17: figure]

Figure 9: The main interface window for Rover 3. Sensor inputs along the top are displayed in millivolts when in debug mode or milliTorr/degrees celcius when not. Each relay control has its own row in the bottom half. Button A is the interlock override with the inset displaying the interlocks disabled icon (exclaimation point) and enabled icon (heart). Button B is the interlock configuration button which will spawn the window displayed in figure 10 and is used to configure interlocks for that relay.

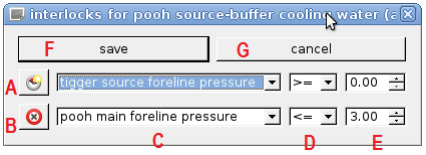
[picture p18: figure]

Figure 10: The interlock configuration window for Rover 3. Button A will create the interlock displayed in the top row. Button B will delete the interlock on that row. Combo boxes and spinbox C, D, and E are the input sensor, logical level on which to trip, and set point respectively. Remember that true statements cause the interlock to trip and shut the relay off. Button F will commit the current changes and button G will discard them.

14

## 6 Troubleshooting Guide

Here we will outline the basic problems and solutions that have been observed during design and assembly. This is by no means a complete guide but will cover the most likely to occur problems.

If you are having problems with Rover your first step should be to rerun roverServer in debug mode: sudo python roverServer.py debug. This will write all the log status to the terminal window and not the log file as well as display all sensor readings in millivolts.

Symptom: the AI channels all read the same and it doesn’t update (eg. 24). This should also be accompanied with an message in the transcript file ’lost connection to ADCs! Retrying in .5s...’.
Cause: connection with the ADC units has been compromised. Solution 0: Check the physical connection between the sensors and the screw terminals.
Solution 1: First check the ribbon cable connection between the RP2 and backplane board.
Solution 2: the 5VDC supply for the backplane may not be working. Check its voltage at the black 2-screw terminal in the lower right quadrant.
Solution 3: Attach a oscilloscope between TP2 and TP0 and between TP3 and TP0. Close RoverServer.py. Execute sudo i2cdetect -y 1. The scope should display 16-bit bursts on both channels (see figure 3). If the logic levels are not sharp edges there is stray capacitance somewhere on either the clock or data lines. This causes the I2C bus to not register the addresses properly. This will be further confirmed by the i2cdetect program not showing an entry for 0x63 or 0x64 (the addresses of the ADCs). First check the connection on R1 and R2. These are pull-up resistors that should improve this voltage timing. Next check the connections on the I2C clock and data wires coming from the RP2 breakout to the ADCs (orange and green).

Symptom: python error - maximum recursion depth exceeded Cause: this is an antiquated version of roverServer.py which uses a recursive function to poll the ADCs in a thread.
Solution 0: Make sure that someone didn’t accidentally revert back to this recursive function. The class that does the ADC acquisition in roverServer.py should be a subclass of thread and should not end with a call to itself.

Symptom: turning a relay off is not actually toggling the device Cause: the relay control line is not working. A few malfunctioning devices could be causing this.

15

Solution 0: Check your connections to devices at the screw terminals. See figure 8. If they are all connected proceed.
Solution 1: First check the ribbon cable connection between the RP2 and backplane board.
Solution 2: the 5VDC supply for the backplane may not be working. Check its voltage at the black 2-screw terminal in the lower right quadrant.
Solution 3: Attach a oscilloscope between TP1 and TP0. This will be observing the clock pin sent to the 574 chips. The 574 will only update its output to match its input when this pin is clocked low to high. Toggle a device in roverServer.py. Does the scope show a clocking event? If no, check the connection between RP2 GPIO pin #4 and pin #11 on each of the 574s. If that is connected, check the source code for roverServer.py and make sure there is a method defined clockPin and it is being sent to each digitalOutput object upon initialization. If the 574s are both being clocked and their outputs are indeed not updating then the chip is faulty and needs to be replaced. Solution 4: If the problem is localized to the Crydom 120VAC relays make sure that you are connecting a load across the relay’s AC terminals. These relays won’t actually power unless it sees a load and a DVM doesn’t count!

16

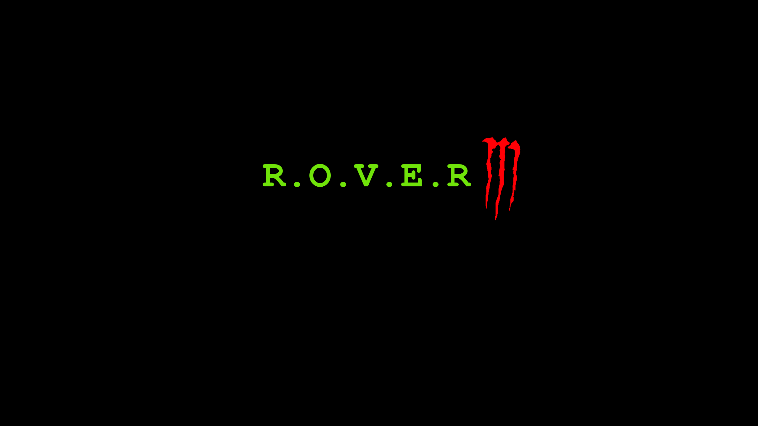
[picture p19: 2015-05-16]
background.png

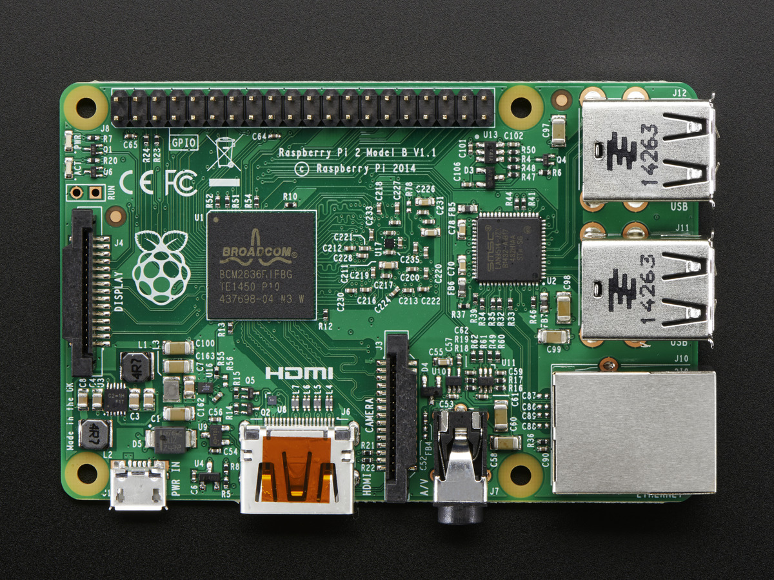
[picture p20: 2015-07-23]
documentation/RP2top.jpg

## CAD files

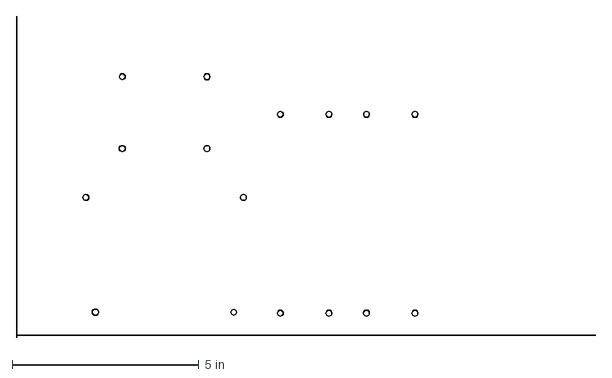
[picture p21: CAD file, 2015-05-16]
documentation/panelHolePattern.dxf
15.5 x 8.60 in

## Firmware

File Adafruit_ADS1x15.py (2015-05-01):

#!/usr/bin/python

import time
import smbus
from Adafruit_I2C import Adafruit_I2C

# ===========================================================================
# ADS1x15 Class
#
# Originally written by K. Townsend, Adafruit (https://github.com/adafruit/Adafruit-Raspberry-Pi-Python-Code/tree/master/Adafruit_ADS1x15)
# Updates and new functions implementation by Pedro Villanueva, 03/2013.
# The only error in the original code was in line 57:
#              __ADS1015_REG_CONFIG_DR_920SPS    = 0x0050
# should be 
#              __ADS1015_REG_CONFIG_DR_920SPS    = 0x0060     
#
# NOT IMPLEMENTED: Conversion ready pin, page 15 datasheet.
# ===========================================================================

class ADS1x15:
  i2c = None

  # IC Identifiers
  __IC_ADS1015                      = 0x00
  __IC_ADS1115                      = 0x01

  # Pointer Register
  __ADS1015_REG_POINTER_MASK        = 0x03
  __ADS1015_REG_POINTER_CONVERT     = 0x00
  __ADS1015_REG_POINTER_CONFIG      = 0x01
  __ADS1015_REG_POINTER_LOWTHRESH   = 0x02
  __ADS1015_REG_POINTER_HITHRESH    = 0x03

  # Config Register
  __ADS1015_REG_CONFIG_OS_MASK      = 0x8000
  __ADS1015_REG_CONFIG_OS_SINGLE    = 0x8000  # Write: Set to start a single-conversion
  __ADS1015_REG_CONFIG_OS_BUSY      = 0x0000  # Read: Bit = 0 when conversion is in progress
  __ADS1015_REG_CONFIG_OS_NOTBUSY   = 0x8000  # Read: Bit = 1 when device is not performing a conversion

  __ADS1015_REG_CONFIG_MUX_MASK     = 0x7000
  __ADS1015_REG_CONFIG_MUX_DIFF_0_1 = 0x0000  # Differential P = AIN0, N = AIN1 (default)
  __ADS1015_REG_CONFIG_MUX_DIFF_0_3 = 0x1000  # Differential P = AIN0, N = AIN3
  __ADS1015_REG_CONFIG_MUX_DIFF_1_3 = 0x2000  # Differential P = AIN1, N = AIN3
  __ADS1015_REG_CONFIG_MUX_DIFF_2_3 = 0x3000  # Differential P = AIN2, N = AIN3
  __ADS1015_REG_CONFIG_MUX_SINGLE_0 = 0x4000  # Single-ended AIN0
  __ADS1015_REG_CONFIG_MUX_SINGLE_1 = 0x5000  # Single-ended AIN1
  __ADS1015_REG_CONFIG_MUX_SINGLE_2 = 0x6000  # Single-ended AIN2
  __ADS1015_REG_CONFIG_MUX_SINGLE_3 = 0x7000  # Single-ended AIN3

  __ADS1015_REG_CONFIG_PGA_MASK     = 0x0E00
  __ADS1015_REG_CONFIG_PGA_6_144V   = 0x0000  # +/-6.144V range
  __ADS1015_REG_CONFIG_PGA_4_096V   = 0x0200  # +/-4.096V range
  __ADS1015_REG_CONFIG_PGA_2_048V   = 0x0400  # +/-2.048V range (default)
  __ADS1015_REG_CONFIG_PGA_1_024V   = 0x0600  # +/-1.024V range
  __ADS1015_REG_CONFIG_PGA_0_512V   = 0x0800  # +/-0.512V range
  __ADS1015_REG_CONFIG_PGA_0_256V   = 0x0A00  # +/-0.256V range

  __ADS1015_REG_CONFIG_MODE_MASK    = 0x0100
  __ADS1015_REG_CONFIG_MODE_CONTIN  = 0x0000  # Continuous conversion mode
  __ADS1015_REG_CONFIG_MODE_SINGLE  = 0x0100  # Power-down single-shot mode (default)

  __ADS1015_REG_CONFIG_DR_MASK      = 0x00E0  
  __ADS1015_REG_CONFIG_DR_128SPS    = 0x0000  # 128 samples per second
  __ADS1015_REG_CONFIG_DR_250SPS    = 0x0020  # 250 samples per second
  __ADS1015_REG_CONFIG_DR_490SPS    = 0x0040  # 490 samples per second
  __ADS1015_REG_CONFIG_DR_920SPS    = 0x0060  # 920 samples per second
  __ADS1015_REG_CONFIG_DR_1600SPS   = 0x0080  # 1600 samples per second (default)
  __ADS1015_REG_CONFIG_DR_2400SPS   = 0x00A0  # 2400 samples per second
  __ADS1015_REG_CONFIG_DR_3300SPS   = 0x00C0  # 3300 samples per second (also 0x00E0)

  __ADS1115_REG_CONFIG_DR_8SPS      = 0x0000  # 8 samples per second
  __ADS1115_REG_CONFIG_DR_16SPS     = 0x0020  # 16 samples per second
  __ADS1115_REG_CONFIG_DR_32SPS     = 0x0040  # 32 samples per second
  __ADS1115_REG_CONFIG_DR_64SPS     = 0x0060  # 64 samples per second
  __ADS1115_REG_CONFIG_DR_128SPS    = 0x0080  # 128 samples per second
  __ADS1115_REG_CONFIG_DR_250SPS    = 0x00A0  # 250 samples per second (default)
  __ADS1115_REG_CONFIG_DR_475SPS    = 0x00C0  # 475 samples per second
  __ADS1115_REG_CONFIG_DR_860SPS    = 0x00E0  # 860 samples per second

  __ADS1015_REG_CONFIG_CMODE_MASK   = 0x0010
  __ADS1015_REG_CONFIG_CMODE_TRAD   = 0x0000  # Traditional comparator with hysteresis (default)
  __ADS1015_REG_CONFIG_CMODE_WINDOW = 0x0010  # Window comparator

  __ADS1015_REG_CONFIG_CPOL_MASK    = 0x0008
  __ADS1015_REG_CONFIG_CPOL_ACTVLOW = 0x0000  # ALERT/RDY pin is low when active (default)
  __ADS1015_REG_CONFIG_CPOL_ACTVHI  = 0x0008  # ALERT/RDY pin is high when active

  __ADS1015_REG_CONFIG_CLAT_MASK    = 0x0004  # Determines if ALERT/RDY pin latches once asserted
  __ADS1015_REG_CONFIG_CLAT_NONLAT  = 0x0000  # Non-latching comparator (default)
  __ADS1015_REG_CONFIG_CLAT_LATCH   = 0x0004  # Latching comparator

  __ADS1015_REG_CONFIG_CQUE_MASK    = 0x0003
  __ADS1015_REG_CONFIG_CQUE_1CONV   = 0x0000  # Assert ALERT/RDY after one conversions
  __ADS1015_REG_CONFIG_CQUE_2CONV   = 0x0001  # Assert ALERT/RDY after two conversions
  __ADS1015_REG_CONFIG_CQUE_4CONV   = 0x0002  # Assert ALERT/RDY after four conversions
  __ADS1015_REG_CONFIG_CQUE_NONE    = 0x0003  # Disable the comparator and put ALERT/RDY in high state (default)
  
  
  # Dictionaries with the sampling speed values
  # These simplify and clean the code (avoid the abuse of if/elif/else clauses)
  spsADS1115 = {
    8:__ADS1115_REG_CONFIG_DR_8SPS,
    16:__ADS1115_REG_CONFIG_DR_16SPS,
    32:__ADS1115_REG_CONFIG_DR_32SPS,
    64:__ADS1115_REG_CONFIG_DR_64SPS,
    128:__ADS1115_REG_CONFIG_DR_128SPS,
    250:__ADS1115_REG_CONFIG_DR_250SPS,
    475:__ADS1115_REG_CONFIG_DR_475SPS,
    860:__ADS1115_REG_CONFIG_DR_860SPS
  }    
  spsADS1015 = {
    128:__ADS1015_REG_CONFIG_DR_128SPS,
    250:__ADS1015_REG_CONFIG_DR_250SPS,
    490:__ADS1015_REG_CONFIG_DR_490SPS,
    920:__ADS1015_REG_CONFIG_DR_920SPS,
    1600:__ADS1015_REG_CONFIG_DR_1600SPS,
    2400:__ADS1015_REG_CONFIG_DR_2400SPS,
    3300:__ADS1015_REG_CONFIG_DR_3300SPS
  }
  # Dictionariy with the programable gains
  pgaADS1x15 = {
    6144:__ADS1015_REG_CONFIG_PGA_6_144V,
    4096:__ADS1015_REG_CONFIG_PGA_4_096V,
    2048:__ADS1015_REG_CONFIG_PGA_2_048V,
    1024:__ADS1015_REG_CONFIG_PGA_1_024V,
    512:__ADS1015_REG_CONFIG_PGA_0_512V,
    256:__ADS1015_REG_CONFIG_PGA_0_256V
  }    
  

  # Constructor
  def __init__(self, address=0x48, ic=__IC_ADS1015, debug=False):
    # Depending on if you have an old or a new Raspberry Pi, you
    # may need to change the I2C bus.  Older Pis use SMBus 0,
    # whereas new Pis use SMBus 1.  If you see an error like:
    # 'Error accessing 0x48: Check your I2C address '
    # change the SMBus number in the initializer below!
    self.i2c = Adafruit_I2C(address)
    self.address = address
    self.debug = debug

    # Make sure the IC specified is valid
    if ((ic < self.__IC_ADS1015) | (ic > self.__IC_ADS1115)):
      if (self.debug):
        print "ADS1x15: Invalid IC specfied: %h" % ic
      return -1
    else:
      self.ic = ic
        
    # Set pga value, so that getLastConversionResult() can use it,
    # any function that accepts a pga value must update this.
    self.pga = 6144    
  
    
  def readADCSingleEnded(self, channel=0, pga=6144, sps=250):
    "Gets a single-ended ADC reading from the specified channel in mV. \
    The sample rate for this mode (single-shot) can be used to lower the noise \
    (low sps) or to lower the power consumption (high sps) by duty cycling, \
    see datasheet page 14 for more info. \
    The pga must be given in mV, see page 13 for the supported values."
    
    # With invalid channel return -1
    if (channel > 3):
      if (self.debug):
        print "ADS1x15: Invalid channel specified: %d" % channel
      return -1
    
    # Disable comparator, Non-latching, Alert/Rdy active low
    # traditional comparator, single-shot mode
    config = self.__ADS1015_REG_CONFIG_CQUE_NONE    | \
             self.__ADS1015_REG_CONFIG_CLAT_NONLAT  | \
             self.__ADS1015_REG_CONFIG_CPOL_ACTVLOW | \
             self.__ADS1015_REG_CONFIG_CMODE_TRAD   | \
             self.__ADS1015_REG_CONFIG_MODE_SINGLE    

    # Set sample per seconds, defaults to 250sps
    # If sps is in the dictionary (defined in init) it returns the value of the constant
    # othewise it returns the value for 250sps. This saves a lot of if/elif/else code!
    if (self.ic == self.__IC_ADS1015):
      config |= self.spsADS1015.setdefault(sps, self.__ADS1015_REG_CONFIG_DR_1600SPS)
    else:
      if ( (sps not in self.spsADS1115) & self.debug):	  
	print "ADS1x15: Invalid pga specified: %d, using 6144mV" % sps     
      config |= self.spsADS1115.setdefault(sps, self.__ADS1115_REG_CONFIG_DR_250SPS)

    # Set PGA/voltage range, defaults to +-6.144V
    if ( (pga not in self.pgaADS1x15) & self.debug):	  
      print "ADS1x15: Invalid pga specified: %d, using 6144mV" % sps     
    config |= self.pgaADS1x15.setdefault(pga, self.__ADS1015_REG_CONFIG_PGA_6_144V)
    self.pga = pga

    # Set the channel to be converted
    if channel == 3:
      config |= self.__ADS1015_REG_CONFIG_MUX_SINGLE_3
    elif channel == 2:
      config |= self.__ADS1015_REG_CONFIG_MUX_SINGLE_2
    elif channel == 1:
      config |= self.__ADS1015_REG_CONFIG_MUX_SINGLE_1
    elif channel == 0:
      config |= self.__ADS1015_REG_CONFIG_MUX_SINGLE_0
    else:
        return

    # Set 'start single-conversion' bit
    config |= self.__ADS1015_REG_CONFIG_OS_SINGLE

    # Write config register to the ADC
    bytes = [(config >> 8) & 0xFF, config & 0xFF]
    self.i2c.writeList(self.__ADS1015_REG_POINTER_CONFIG, bytes)

    # Wait for the ADC conversion to complete
    # The minimum delay depends on the sps: delay >= 1/sps
    # We add 0.1ms to be sure
    delay = 1.0/sps+0.0001
    time.sleep(delay)

    # Read the conversion results
    result = self.i2c.readList(self.__ADS1015_REG_POINTER_CONVERT, 2)
    if (self.ic == self.__IC_ADS1015):
    	# Shift right 4 bits for the 12-bit ADS1015 and convert to mV
    	return ( ((result[0] << 8) | (result[1] & 0xFF)) >> 4 )*pga/2048.0
    else:
	# Return a mV value for the ADS1115
	# (Take signed values into account as well)
	val = (result[0] << 8) | (result[1])
	if val > 0x7FFF:
	  return (val - 0xFFFF)*pga/32768.0
	else:
	  return ( (result[0] << 8) | (result[1]) )*pga/32768.0
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

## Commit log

2015-04-01 initialized project. starting with a (mostly) working GUI. no device functionality working yet.
2015-04-01 added logs subfolder
    [roverStatus.tsv, roverTranscript.tsv]
2015-04-07 added sitzlabexpcontrol libraries for file creation and LED widget
2015-05-01 removed old log files
    [roverStatus.tsv, roverTranscript.tsv]
2015-05-14 adjusted pin values based on soldered version of breakout board. GUI is laid out matching the order of screw terminals.
2015-05-14 added DO clock pin functionality. each time a new DO value is written (a unit is toggled on or off) pin 4 is cycled high then low in the writeState method. this clocks the 574 chip so that it latches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
2015-05-16 attempted bug fix: threading the A2D would previously hit a max recursion depth error. this was probably because I was threading a recursive function. now there is a single thread with a while loop t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
2015-05-16 added documentation folder with circuit diagrams and some datasheets. not complete yet.
    [circuitDiagrams.dsn, panelHolePattern.dxf]
2015-05-16 fix works! minor bug fixes ontop of the initial idea of threading a single while loop for ADC.
2015-06-02 added lab power sense functionality.
2015-07-23 adjusted debug mode to now display voltages (not mapped) in GUI.
2015-07-23 last version of the documentation.
    [circuitDiagrams.dsn]
